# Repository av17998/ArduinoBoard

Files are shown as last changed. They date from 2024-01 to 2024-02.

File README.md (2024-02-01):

# AATL Go-Baby-Go Arduino Hat Board

### Designed as a hat board for an Arduino Mega to distribute power and simplify sensor and motor connections. 

## Overall Functions

<p align="center">
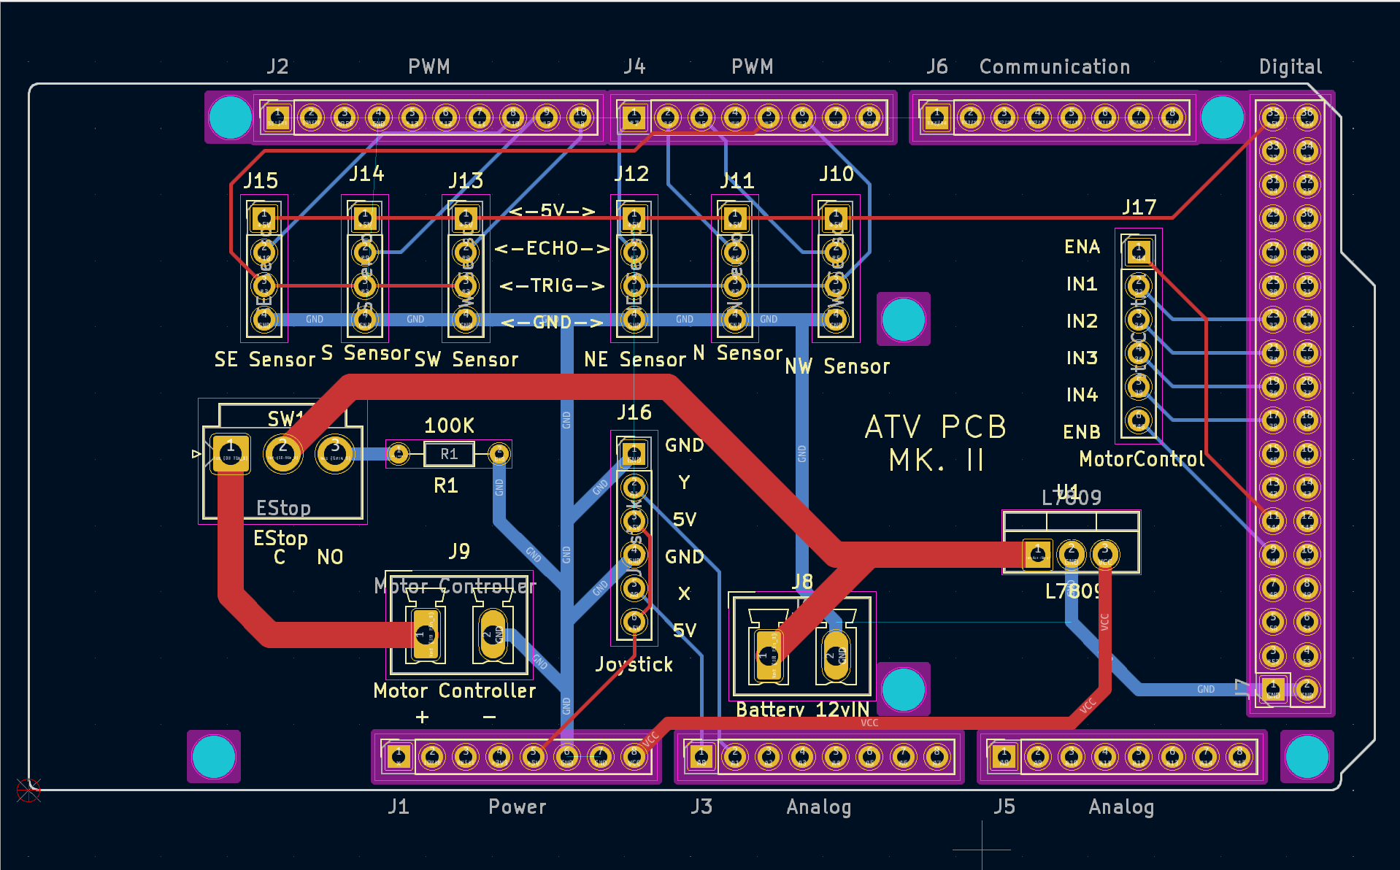
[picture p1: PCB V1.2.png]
Hat Board V1.2
  
</p>

For this design, the input voltage is 12V, which is split to a linear regulator and to the motor controller for power. The 9V regulator steps down the voltage to input into the Vin pin on the Arduino mega, which will output 5V, which will power the sensors and joysticks. 

There are six pin headers for HCSR04 Ultrasonic Sensors. These sensors are connected in two arrays, one forward and one backwards, designated by "North" and "South". Each array contains three sensors to get a large angle to sense objects in front of or behind the car. The current itteration of the code (uploaded in seperate repo linked below), the sensors are triggered to detect distance depending on which direction the input joystick is moving. 

The joystick is a two axis joystick to be used as the only input method for the vehicle. The only info relevant to this repo is that the joystick takes two 5V and two ground inputs, with one pin each for x and y inputs. 

The motor controller is getting 12V power through a single pole double through EStop switch. When in the normally open position, the motor controller will get 12V power to drive the motors. The motor controller is also connected with the other 6 pin header, which contains enable pins for each motor, and two input pins for each motor. 

## GBR and DRL Files

These files are zipped in zip folders labled by their itteration number. Each of these zip files can be uploaded to a PCB printing website or a GBR file viewer and the PCB designs should be fully portrayed.

## Code Link

https://github.com/av17998/Baby-Car-Code

Design property of Purdue Polytechnic Institute 

## V1.2 Changes

There was an error made in the design that when the EStop switch was in the normally common position, the 12V will be connected straight to ground, so a change has been implemented to connect these pins through a 100k resistor.

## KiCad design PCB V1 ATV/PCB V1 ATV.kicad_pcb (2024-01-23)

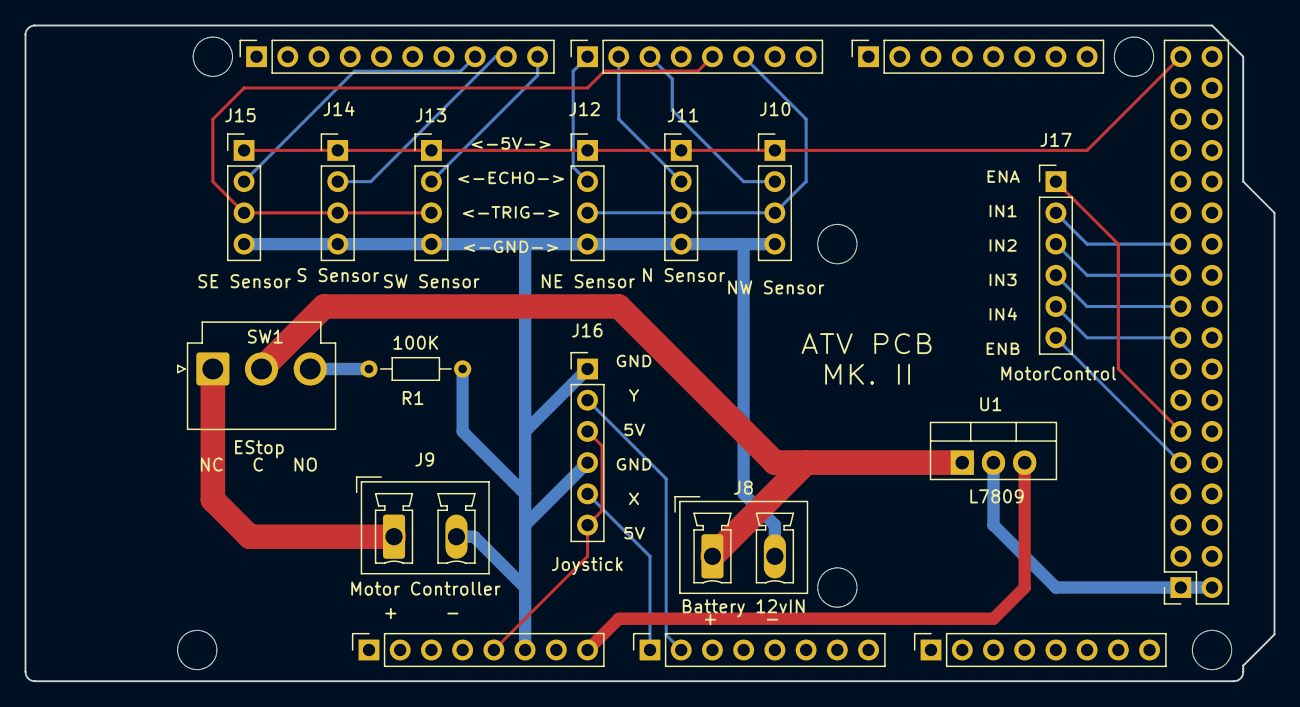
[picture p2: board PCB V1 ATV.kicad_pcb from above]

Board: 2 copper layers, 101.6 x 53.3 mm, 26 parts (0 on the bottom side), 24 nets.

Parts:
EStop: SW1; JST_VH_B3P-VH-B_1x03_P3.96mm_Vertical
J1: Power; PinSocket_1x08_P2.54mm_Vertical
J2: PWM; PinSocket_1x10_P2.54mm_Vertical
J3, J5: Analog; PinSocket_1x08_P2.54mm_Vertical
J4: PWM; PinSocket_1x08_P2.54mm_Vertical
J6: Communication; PinSocket_1x08_P2.54mm_Vertical
J7: Digital; PinSocket_2x18_P2.54mm_Vertical
J8: Battery 12vIN; Custom 2 Part Phoenix Connector
Joystick: J16; PinHeader_1x06_P2.54mm_Vertical
L7809: U1; TO-220-3_Vertical
MH1, MH2, MH3, MH4, MH5, MH6: MountingHole_3.2mm
Motor Controller : J9; Custom 2 Part Phoenix Connector
MotorControl: J17; PinHeader_1x06_P2.54mm_Vertical
N Sensor: J11; PinHeader_1x04_P2.54mm_Vertical
NE Sensor: J12; PinHeader_1x04_P2.54mm_Vertical
NW Sensor: J10; PinHeader_1x04_P2.54mm_Vertical
R1: 100K; R_Axial_DIN0204_L3.6mm_D1.6mm_P7.62mm_Horizontal
S Sensor: J14; PinHeader_1x04_P2.54mm_Vertical
SE Sensor: J15; PinHeader_1x04_P2.54mm_Vertical
SW Sensor: J13; PinHeader_1x04_P2.54mm_Vertical

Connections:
+5V: J1.5, J7.35, J7.36, Joystick.3, Joystick.6, N Sensor.1, NE Sensor.1, NW Sensor.1, S Sensor.1, SE Sensor.1, SW Sensor.1
/32: J7.23, MotorControl.2
/34: J7.21, MotorControl.3
/36: J7.19, MotorControl.4
/38: J7.17, MotorControl.5
/*2: J4.6, N Sensor.3, NE Sensor.3, NW Sensor.3
/*3: J4.5, S Sensor.3, SE Sensor.3, SW Sensor.3
/*5: J4.3, NW Sensor.2
/*6: J4.2, N Sensor.2
/*7: J4.1, NE Sensor.2
/*8: J2.10, SW Sensor.2
/*9: J2.9, S Sensor.2
/*10: J2.8, SE Sensor.2
/*44: J7.11, MotorControl.1
/*46: J7.9, MotorControl.6
/A0: J3.1, Joystick.5
/A1: J3.2, Joystick.2
/SCL/21: J2.1, J6.8
/SDA/20: J2.2, J6.7
GND: J1.6, J1.7, J2.4, J7.1, J7.2, J8.2, Joystick.1, Joystick.4, L7809.2 (GND), Motor Controller.2, N Sensor.4, NE Sensor.4, NW Sensor.4, R1.2, S Sensor.4, SE Sensor.4, SW Sensor.4
unnamed: EStop.2 (B), J8.1, L7809.1 (IN)
unnamed: EStop.1 (A), Motor Controller.1
unnamed: EStop.3 (C), R1.1
VCC: J1.8, L7809.3 (OUT)

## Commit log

2024-01-09 Initial Commit
    V1 of Board
    [PCB V1 ATV-B_Cu.gbr, PCB V1 ATV-B_Fab.gbr, PCB V1 ATV-B_Mask.gbr, PCB V1 ATV-B_Paste.gbr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]
2024-01-18 V2.0
    Added resistor between estop and ground
    [PCB V1 ATV.kicad_pcb, PCB V1 ATV.kicad_sch]
2024-01-23 V1.2
    Updated the board to fit the 2 part phoenix connectors, added a resistor, and added more silkscreen. Also removed .gbr and .drl files
    [PCB V1 ATV-B_Cu.gbr, PCB V1 ATV-B_Fab.gbr, PCB V1 ATV-B_Mask.gbr, PCB V1 ATV-B_Paste.gbr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]
2024-01-23 V1.2.1
    Updated the silkscreens
    [PCB V1 ATV.kicad_pcb]
2024-02-01 Adding PCB Image
    Updated backups and PCB Image added
